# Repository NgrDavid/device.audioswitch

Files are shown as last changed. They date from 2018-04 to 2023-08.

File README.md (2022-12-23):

## Harp AudioSwitch ##

This is a multiplexer device that allows an analog input signal to be forwarded to several output channels. It allows forwarding an audio signal to a single speaker or a combination of speakers. The configuration of speakers can be predefined by software or by using a set of digital inputs.

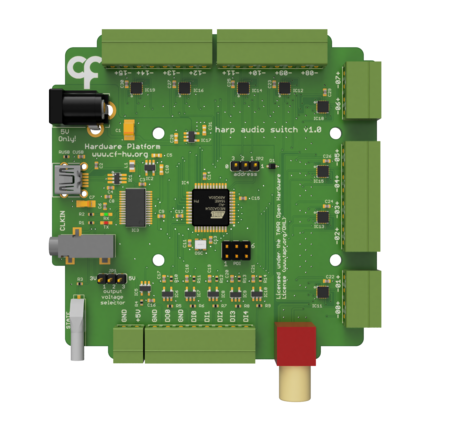
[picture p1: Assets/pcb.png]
harpaudioswitch


### Key Features ###

* Configuration of up to 15 speakers (depending on the input signal strength)
* Several speakers can be activated concurrently

### Connectivity ###

* 1x stereo jack for clock sync input (CLKIN)
* 1x USB (for computer) 1x power barrel connector jack (5V only) 1x screw terminal connector for output power (GND, +5V) 1x screw terminal connector for speaker configuration (GND, DOUT0, GND, DIN0 to DIN4)

## Interface ##

The interface with the Harp board can be done through [Bonsai](https://bonsai-rx.org/) or a dedicated GUI (Graphical User Interface).

In order to use this GUI, there are some software that needs to be installed:

1 - Install the [drivers](https://bitbucket.org/fchampalimaud/downloads/downloads/UsbDriver-2.12.26.zip).

2 - Install the [runtime](https://bitbucket.org/fchampalimaud/downloads/downloads/Runtime-1.0.zip).

3 - Reboot the computer.

4 - Install the [GUI](https://bitbucket.org/fchampalimaud/downloads/downloads/Harp%20Audio%20Switch%20v1.0.0.zip).

## Licensing ##

Each subdirectory will contain a license or, possibly, a set of licenses if it involves both hardware and software.

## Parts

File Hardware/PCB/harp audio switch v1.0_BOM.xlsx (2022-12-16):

Part(s) | Quantity | Description | Distributor | Part. No.
IC1 | 1 | ESD Protection Low Cap | Mouser | 511-USBLC6-2SC6Y
IC2, IC17 | 2 | LDO 250mA Ultra-Lo Noise LDO Reg 3V | Mouser | 595-LP5907MFX-3.0NPB
IC3 | 1 | IC USB USB to Serial UART Enhanced IC SSOP-28 | Mouser | 895-FT232RL
IC4 | 1 | Microcontroladores de 8 bits - MCU 44TQFP, IND TEMP GREEN, 1.6-3.6V | Mouser | 556-ATXMEGA128A4U-AU
IC5, IC6, IC7, IC8, IC9, IC10 | 6 | Buffers e line drivers 1.65-5.5V Single Non-Inverting TTL | Mouser | 863-M74VHC1GT50DTT1G
IC10, IC11, IC12, IC13, IC14, IC15, IC16, IC18 | 8 | CIs de Chave Analógica Quad-SPDT Clickless Audio Switch | Mouser | 700-MAX4910ETE
 | 0 | LDO 250mA Ultra-Lo Noise LDO Reg | Mouser | 595-LP5907MFX-2.8NPB
C3, C4 | 2 | CAP CER 47pF 50V ±5% C0G 0402 | Mouser | 77-VJ0402A470JXACBC
CUSB | 1 | CAP CER 4.7nF 100V ±10% X7R 0402 | Mouser | 81-GRM155R72A472KA01
C22, C23, C24, C25, C26, C27, C29, C30 | 8 | CAP CER 10nF 10V ±10% X5R 0402 | Mouser | 81-GRM155R61A103KA1D
C2, C6, C8, C9, C11, C12, C14, C15, C16, C17, C18, C19, C20, C21 | 14 | CAP CER 100nF 10V X5R 0402 | REEL | REEL
C13 | 1 | CAP CER 0.33uF 10V ±10% X5R 0402 | Mouser | GRM155R61A334KE15D
C7 | 1 | CAP TAN 4.7uF 16V ±10% 1206 | Mouser | 80-T491A475K16AT7280
C5, C10, C28, C31 | 4 | CAP CER 10uF 10V ±10% X5R 0603 | Mouser | 81-GRM188R61A106KE9D
C1 | 1 | CAP TAN 22uF 20V ±10% 1210 | Mouser | 667-20TQC22MYFB
R4, R10, R11, R12, R13, R14 | 6 | RES SMD 33Ω 5% 0402 | Mouser | 667-ERJ-2GEJ330X
R3 | 1 | RES SMD 68Ω 5% 0402 | Mouser | 71-CRCW0402-68-E3
R5, R6, R7, R8, R9 | 5 | RES SMD 100kΩ 1% 0402 | REEL | REEL
RUSB | 1 | RES SMD 1MΩ 1% 0402 | Mouser | 652-CR0402FX-1004GLF
D1 | 1 | DIODE SCHOTTKY 30V 1A SOD323 | Mouser | 621-SDM100K30L-7
STATE | 1 | LED, Green, 1.6mm x 0.8mm, 566 nm, 2.1 V, 20 mA, 15 mcd | Mouser | 78-TLMP1100-GS08
OSC | 1 | 32MHz 10ppm | Mouser | 998-1001CI5032.0000T
CLKIN | 1 | SMT 3.5 STEREO REEL | Mouser | 502-35RASMT2BHNTRX
L1 | 1 | 40ohms 100MHz 1.5A Monolithic 0805 SMD | Mouser | 875-MI0805K400R-10
PDI | 1 | 6P DR UNSHRD HRD | Mouser | 649-67996-206HLF
J1 | 1 | Conectores de fono RCA 1 POS RA PHONO JACK | Mouser | 502-PJRAN1X1U03AUX
USB | 1 | UX60-MB-5S8 | Mouser | 798-UX60-MB-5S8
USB Cable | 1 | USB A - MINI-B 1M BLACK | Mouser | 538-88732-8602
 | 1 | Tubos de Luz LED CML LIGHTPIPE | Mouser | 606-7513D2-L
JACK | 1 | CC 2.5mm LOCKING | Mouser | 161-0725-E
JP1, JP2 | 2 | 3POS Gold Male | Mouser | 649-68001-203HLF
 | 2 | SHUNT JUMPER, 2POS | Farnell | 2396301
WALL ADAPTER | 1 | AC/DC Power Supply, 1 Output, 5 W, 5 V, 1 A | Farnell | 1971787
X1 | 1 | 20.1550M/2-E - Pluggable Terminal Block, 3.5 mm, 2 Ways, 28 AWG, 16 AWG, 1.5 mm², Screw | Farnell | 2575215
X5, X7 | 2 | 20.1550M/4-E - Pluggable Terminal Block, 3.5 mm, 4 Ways, 28 AWG, 16 AWG, 1.5 mm², Screw | Farnell | 2575217
X2, X3, X4, X6 | 4 | 20.1550M/8-E - Pluggable Terminal Block, 3.5 mm, 8 Ways, 28 AWG, 16 AWG, 1.5 mm², Screw | Farnell | 2575220
 | 1 | 20.155MH/2-E - Terminal Block, Horizontal, Header, 3.5 mm, 2 Ways, 10 A | Farnell | 2517858
 | 2 | 20.155MH/4-E - Terminal Block, Horizontal, Header, 3.5 mm, 4 Ways, 10 A | Farnell | 2517860
 | 4 | 20.155MH/8-E - Terminal Block, Horizontal, Header, 3.5 mm, 8 Ways, 10 A | Farnell | 2517863
 | 8 | 1110030 - Nut, Hex, M3, Nylon 6.6, Pack of 50 | Farnell | 1110030
 | 4 | Machine Screw, M3, 10 mm, Nylon (Polyamide), Pan Head Slotted, PK25 | Farnell | 1514410
Components | 106
Licensed under the TAPR Open Hardware License (www.tapr.org/OHL)
Copyright 2017 Artur Silva and Filipe Carvalho

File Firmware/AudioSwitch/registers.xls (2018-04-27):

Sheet: registers
Has event. | When | Type | Array | Array Len. | Register Name | Desciption | Mask Type | Value | Name | Desciption
no |  | U8 | no |  | SOURCE | Source of the board control | mask | (1<<0) | SOURCE
 |  |  |  |  |  |  | group_mask | (0<<0) | USB | Device is controlled by a host computer
 |  |  |  |  |  |  | group_mask | (1<<0) | EXTERNAL | Device is controlled by the digital inputs
yes | When changed by the digital inputs 0-3 | U16 | no |  | CHANNEL_SEL | Enable bit mask of the outputs
yes | When the inputs change (DI0-3 only if they are configured as digital ) | U8 | no |  | DI_STATE | State of the digital inputs | bit | (1<<0) | DI0
 |  |  |  |  |  |  | bit | (1<<1) | DI1
 |  |  |  |  |  |  | bit | (1<<2) | DI2
 |  |  |  |  |  |  | bit | (1<<3) | DI3
 |  |  |  |  |  |  | bit | (1<<4) | DI4
no |  | U8 | no |  | DO | State of the digital output 0 | bit | (1<<0) | DO0
no |  | U8 | no |  | RESERVED0 | Reserved for future use
no |  | U8 | no |  | DI4_CONF | Configuration of digital input 4 (DI4)functionality | mask | (1<<0) | DI4_CONF
 |  |  |  |  |  |  | group_mask | (0<<0) | DI4_DIGITAL
 |  |  |  |  |  |  | group_mask | (1<<0) | DI4_ADDRESS
no |  | U8 | no |  | DO0_CONF | Configuration of the digital output 0 (DO0) funtionality | mask | (1<<0) | DO0_CONF
 |  |  |  |  |  |  | group_mask | (0<<0) | DO_DIGITAL
 |  |  |  |  |  |  | group_mask | (1<<0) | DO_TGL_WHEN_CH_SEL_CHANGE
no |  | U8 | no |  | EVNT_ENABLE | Enable the Events | bit | (1<<0) | EVT_OUTPUT_CHANNEL | Event of register CHANNEL_SEL
 |  |  |  |  |  |  | bit | (1<<1) | EVT_DI_STATE | Event of register DI_STATE

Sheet: meta data
who am I: | 1248
firmware major version: | 1
firmware minor version: | 0
hardware major version: | 1
hardware minor version: | 0
assembly version: | 0
device name: | AudioSwitch

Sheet: ios
Pin Name | PORT | Pin | Direction | Use Input | Out | Out default | Pull | Sense | Int. priority | Int. number | Desciption | Neg. Output
EN0 | PORTA | 0 | output | yes | digital | 0 |  |  |  |  | Enable channel 0 | no
EN1 | PORTA | 1 | output | yes | digital | 0 |  |  |  |  | Enable channel 1 | no
EN2 | PORTA | 2 | output | yes | digital | 0 |  |  |  |  | Enable channel 2 | no
EN3 | PORTA | 3 | output | yes | digital | 0 |  |  |  |  | Enable channel 3 | no
EN4 | PORTA | 4 | output | yes | digital | 0 |  |  |  |  | Enable channel 4 | no
EN5 | PORTA | 5 | output | yes | digital | 0 |  |  |  |  | Enable channel 5 | no
EN6 | PORTA | 6 | output | yes | digital | 0 |  |  |  |  | Enable channel 6 | no
EN7 | PORTA | 7 | output | yes | digital | 0 |  |  |  |  | Enable channel 7 | no
EN8 | PORTD | 0 | output | yes | digital | 0 |  |  |  |  | Enable channel 8 | no
EN9 | PORTD | 1 | output | yes | digital | 0 |  |  |  |  | Enable channel 9 | no
EN10 | PORTD | 2 | output | yes | digital | 0 |  |  |  |  | Enable channel 10 | no
EN11 | PORTD | 3 | output | yes | digital | 0 |  |  |  |  | Enable channel 11 | no
EN12 | PORTD | 4 | output | yes | digital | 0 |  |  |  |  | Enable channel 12 | no
EN13 | PORTD | 5 | output | yes | digital | 0 |  |  |  |  | Enable channel 13 | no
EN14 | PORTD | 6 | output | yes | digital | 0 |  |  |  |  | Enable channel 14 | no
EN15 | PORTD | 7 | output | yes | digital | 0 |  |  |  |  | Enable channel 15 | no
IN0 | PORTB | 0 | input |  |  |  | tristate | both_edges | low | 0 | Decoder bit 0
IN1 | PORTB | 1 | input |  |  |  | tristate | both_edges | low | 0 | Decoder bit 1
IN2 | PORTB | 2 | input |  |  |  | tristate | both_edges | low | 0 | Decoder bit 2
IN3 | PORTB | 3 | input |  |  |  | tristate | both_edges | low | 0 | Decoder bit 3
IN4 | PORTC | 0 | input |  |  |  | tristate | both_edges | low | 0 | Digital Input 4
DO0 | PORTC | 1 | output | yes | digital | 0 |  |  |  |  | Digital output 0 | no
ADD | PORTC | 4 | input |  |  |  | down | both_edges | low | 1 | Address

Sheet: options
Array | Type | Array | Bits type | Direction | Use input | Pull | Sense | Int. priority | Int. number | Int. Mask | Out | Neg. Output
 |  |  |  | input | yes | up | both_edges | low | 0 |  | digital | yes
yes | U8 | yes | bit | output | no | down | rising_edge | med | 1 |  | wire_or | no
no | U16 | no | mask |  |  | tristate | falling_edge | high |  |  | wire_and
 | U32 |  | group_mask |  |  | busholder | low_level | off |  |  | wired_or_pull
 | U64 |  |  |  |  |  | no_interrupt |  |  |  | wired_and_pull
 | I8
 | I16
 | I32
 | I64
 | FLOAT

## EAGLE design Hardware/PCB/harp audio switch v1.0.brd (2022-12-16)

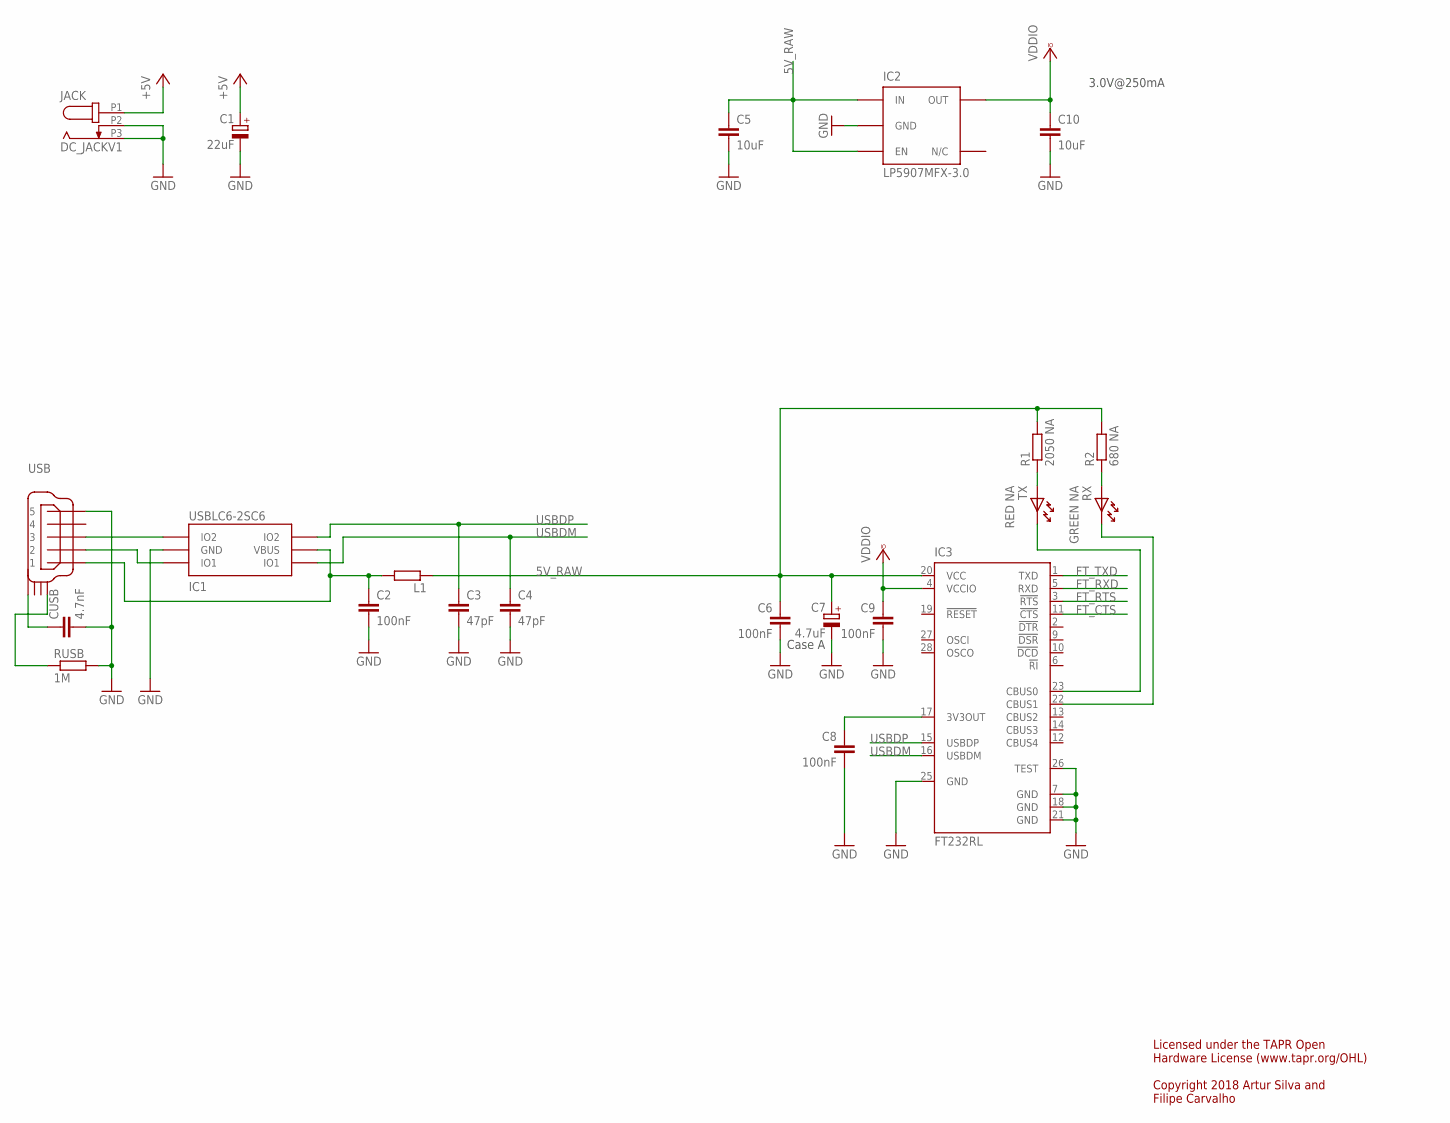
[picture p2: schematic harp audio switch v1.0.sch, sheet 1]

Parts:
C1: 22uF; CAP_100UF_HAND
C2, C6, C8, C9: 100nF; C0402
C3, C4: 47pF; C0402
C5, C10: 10uF; C0603
C7: 4.7uF; A/3216-18W
CUSB: 4.7nF; C0402
IC1: USBLC6-2SC6; SOT23-6L
IC2: LP5907MFX-3.0; TSOT23-5
IC3: FT232RL; SSOP28
JACK: DC_JACKV1; DC_POWER_INPUT
L1: ???; R0805
R1: 2050 NA; R0402
R2: 680 NA; R0402
RUSB: 1M; R0402
RX: GREEN NA; LED_HAND
TX: RED NA; LED_HAND
USB: USB_MINI_B; 240-0002-1

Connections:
5V_RAW: C5.1, C6.1, C7.+, IC2.1 (IN), IC2.3 (EN), IC3.20 (VCC), L1.1, R1.2, R2.2
+5V: C1.+, JACK.P1 (1); also elsewhere on the board
FT_CTS: IC3.11 (!CTS); also elsewhere on the board
FT_RTS: IC3.3 (!RTS); also elsewhere on the board
FT_RXD: IC3.5 (RXD); also elsewhere on the board
FT_TXD: IC3.1 (TXD); also elsewhere on the board
GND: C1.-, C2.2, C3.2, C4.2, C5.2, C6.2, C7.-, C8.2, C9.2, C10.2, CUSB.2, IC1.P$2 (GND), IC2.2 (GND), IC3.7 (GND), IC3.18 (GND), IC3.21 (GND), IC3.25 (GND), IC3.26 (TEST), JACK.P2 (2), JACK.P3 (3), RUSB.2, USB.P$5 (5); also elsewhere on the board
unnamed: C8.1, IC3.17 (3V3OUT)
unnamed: C2.1, IC1.P$5 (VBUS), L1.2, USB.P$1 (1)
unnamed: IC1.P$1 (IO1), USB.P$2 (2)
unnamed: R2.1, RX.A
unnamed: IC3.23 (CBUS0), TX.K
unnamed: IC3.22 (CBUS1), RX.K
unnamed: IC1.P$3 (IO2), USB.P$3 (3)
unnamed: CUSB.1, USB.SHIELD_4
unnamed: RUSB.1, USB.SHIELD_1
unnamed: R1.1, TX.A
USBDM: C4.1, IC1.P$6 (IO1), IC3.16 (USBDM)
USBDP: C3.1, IC1.P$4 (IO2), IC3.15 (USBDP)
VCCIO: C9.1, C10.1, IC2.5 (OUT), IC3.4 (VCCIO); also elsewhere on the board

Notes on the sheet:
Case A
3.0V@250mA
Licensed under the TAPR Open Hardware License (www.tapr.org/OHL) Copyright 2018 Artur Silva and Filipe Carvalho

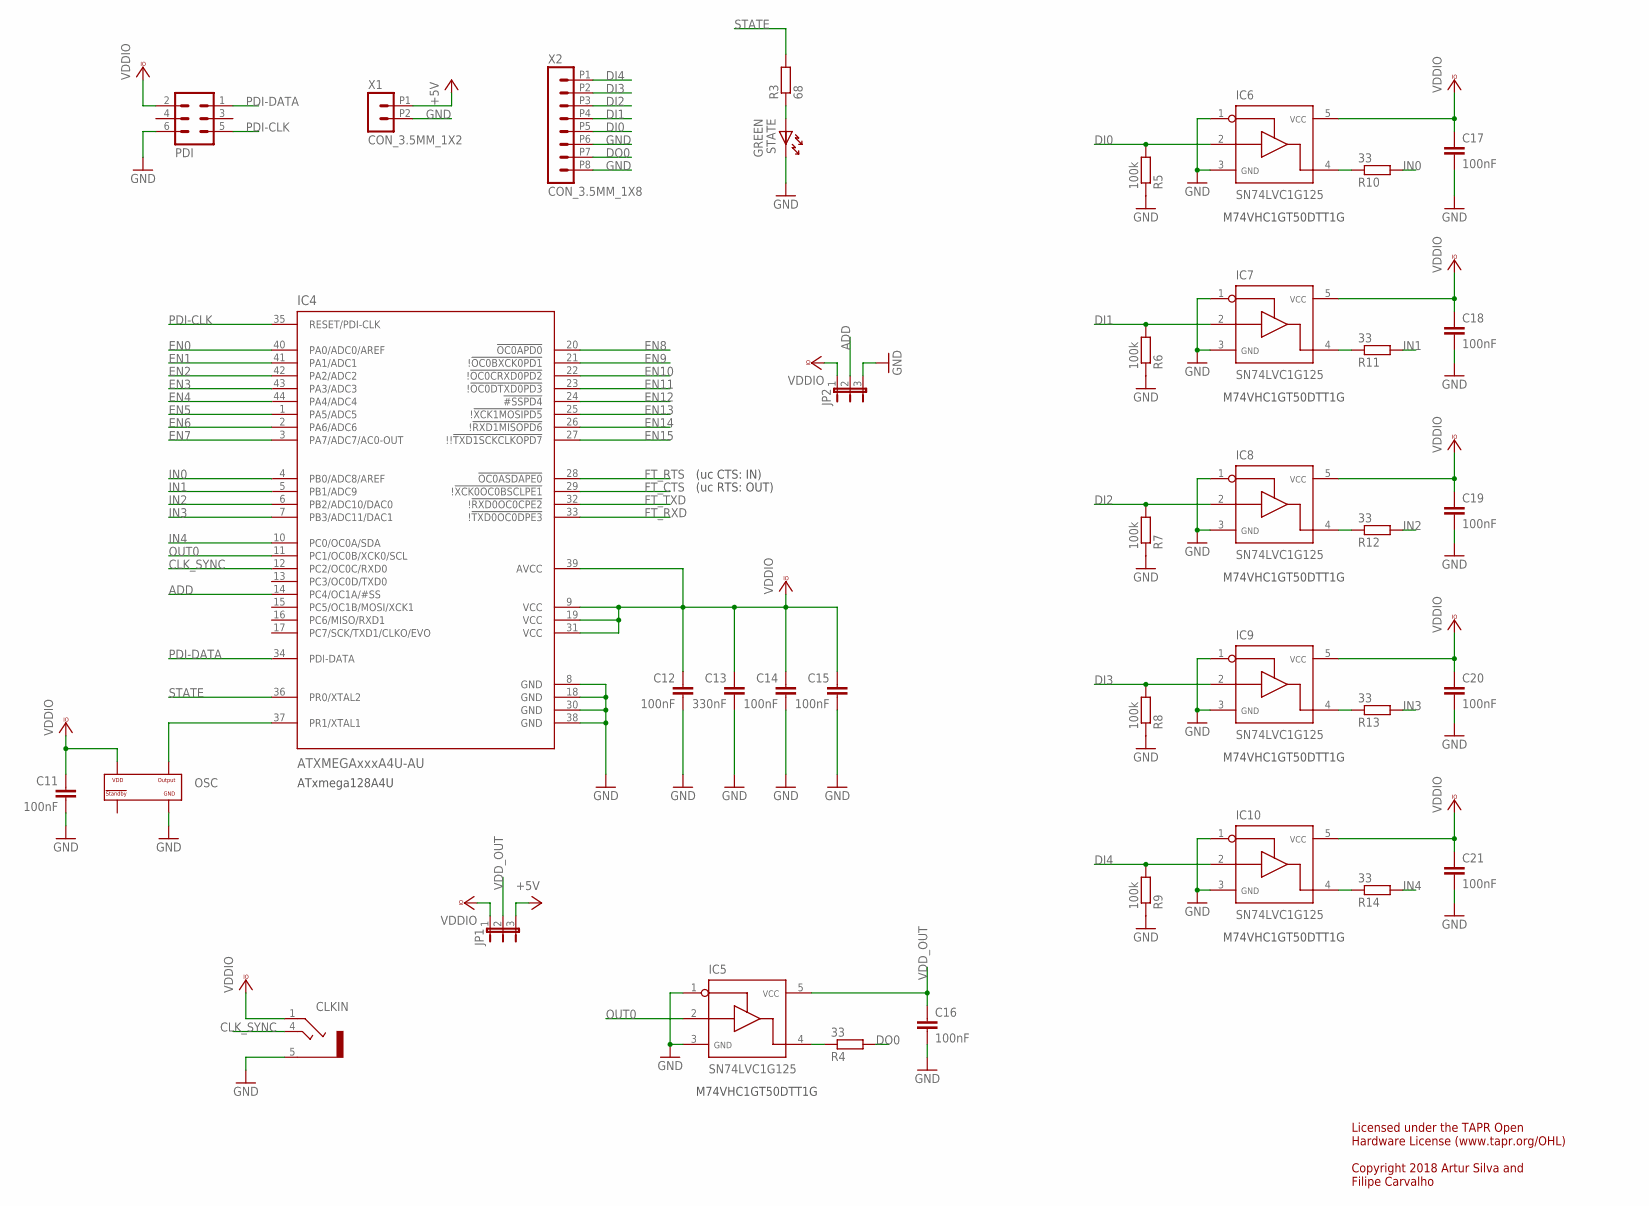
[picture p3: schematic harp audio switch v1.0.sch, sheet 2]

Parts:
C11, C12, C14, C15, C16, C17, C18, C19, C20, C21: 100nF; C0402
C13: 330nF; C0402
CLKIN: STEREO_JACK; 35RASMT2BHNTRX
IC4: ATXMEGAxxxA4U-AU; QFP80P1200X1200X120-44N
IC5, IC6, IC7, IC8, IC9, IC10: SN74LVC1G125; SOT23-5
JP1, JP2: JP2E; JP2
OSC: OSCILLATOR; OSCILLATOR_3.2X2.5
PDI: MA03-2
R3: 68; R0402
R4, R10, R11, R12, R13, R14: 33; R0402
R5, R6, R7, R8, R9: 100k; R0402
STATE: GREEN; LED_HAND
X1: CON_3.5MM_1X2
X2: CON_3.5MM_1X8

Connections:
+5V: JP1.3, X1.P1 (1); also elsewhere on the board
ADD: IC4.14 (PC4/OC1A/#SS), JP2.2
CLK_SYNC: CLKIN.4, IC4.12 (PC2/OC0C/RXD0)
DI0: IC6.2, R5.2, X2.P5 (5)
DI1: IC7.2, R6.2, X2.P4 (4)
DI2: IC8.2, R7.2, X2.P3 (3)
DI3: IC9.2, R8.2, X2.P2 (2)
DI4: IC10.2, R9.2, X2.P1 (1)
DO0: R4.2, X2.P7 (7)
EN0: IC4.40 (PA0/ADC0/AREF); also elsewhere on the board
EN1: IC4.41 (PA1/ADC1); also elsewhere on the board
EN2: IC4.42 (PA2/ADC2); also elsewhere on the board
EN3: IC4.43 (PA3/ADC3); also elsewhere on the board
EN4: IC4.44 (PA4/ADC4); also elsewhere on the board
EN5: IC4.1 (PA5/ADC5); also elsewhere on the board
EN6: IC4.2 (PA6/ADC6); also elsewhere on the board
EN7: IC4.3 (PA7/ADC7/AC0-OUT); also elsewhere on the board
EN8: IC4.20 (!OC0APD0); also elsewhere on the board
EN9: IC4.21 (!!OC0BXCK0PD1); also elsewhere on the board
EN10: IC4.22 (!!OC0CRXD0PD2); also elsewhere on the board
EN11: IC4.23 (!!OC0DTXD0PD3); also elsewhere on the board
EN12: IC4.24 (!#SSPD4); also elsewhere on the board
EN13: IC4.25 (!!XCK1MOSIPD5); also elsewhere on the board
EN14: IC4.26 (!!RXD1MISOPD6); also elsewhere on the board
EN15: IC4.27 (!!!TXD1SCKCLKOPD7); also elsewhere on the board
FT_CTS: IC4.29 (!!XCK0OC0BSCLPE1); also elsewhere on the board
FT_RTS: IC4.28 (!OC0ASDAPE0); also elsewhere on the board
FT_RXD: IC4.33 (!!TXD0OC0DPE3); also elsewhere on the board
FT_TXD: IC4.32 (!!RXD0OC0CPE2); also elsewhere on the board
GND: C11.2, C12.2, C13.2, C14.2, C15.2, C16.2, C17.2, C18.2, C19.2, C20.2, C21.2, CLKIN.5, IC4.8 (GND), IC4.18 (GND), IC4.30 (GND), IC4.38 (GND), IC5.1, IC5.3, IC6.1, IC6.3, IC7.1, IC7.3, IC8.1, IC8.3, IC9.1, IC9.3, IC10.1, IC10.3, JP2.3, OSC.P$2 (GND), PDI.6, R5.1, R6.1, R7.1, R8.1, R9.1, STATE.K, X1.P2 (2), X2.P6 (6), X2.P8 (8); also elsewhere on the board
IN0: IC4.4 (PB0/ADC8/AREF), R10.2
IN1: IC4.5 (PB1/ADC9), R11.2
IN2: IC4.6 (PB2/ADC10/DAC0), R12.2
IN3: IC4.7 (PB3/ADC11/DAC1), R13.2
IN4: IC4.10 (PC0/OC0A/SDA), R14.2
unnamed: IC5.4, R4.1
unnamed: IC7.4, R11.1
unnamed: IC6.4, R10.1
unnamed: IC8.4, R12.1
unnamed: IC9.4, R13.1
unnamed: IC10.4, R14.1
unnamed: R3.1, STATE.A
OSC2: IC4.37 (PR1/XTAL1), OSC.P$3 (OUTPUT)
OUT0: IC4.11 (PC1/OC0B/XCK0/SCL), IC5.2
PDI-CLK: IC4.35 (RESET/PDI-CLK), PDI.5
PDI-DATA: IC4.34 (PDI-DATA), PDI.1
STATE: IC4.36 (PR0/XTAL2), R3.2
VCCIO: C11.1, C12.1, C13.1, C14.1, C15.1, C17.1, C18.1, C19.1, C20.1, C21.1, CLKIN.1, IC4.9 (VCC), IC4.19 (VCC), IC4.31 (VCC), IC4.39 (AVCC), IC6.5, IC7.5, IC8.5, IC9.5, IC10.5, JP1.1, JP2.1, OSC.P$4 (VDD), PDI.2; also elsewhere on the board
VDD_OUT: C16.1, IC5.5, JP1.2

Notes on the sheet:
Licensed under the TAPR Open Hardware License (www.tapr.org/OHL) Copyright 2018 Artur Silva and Filipe Carvalho
(uc CTS: IN)
(uc RTS: OUT)
M74VHC1GT50DTT1G
ATxmega128A4U

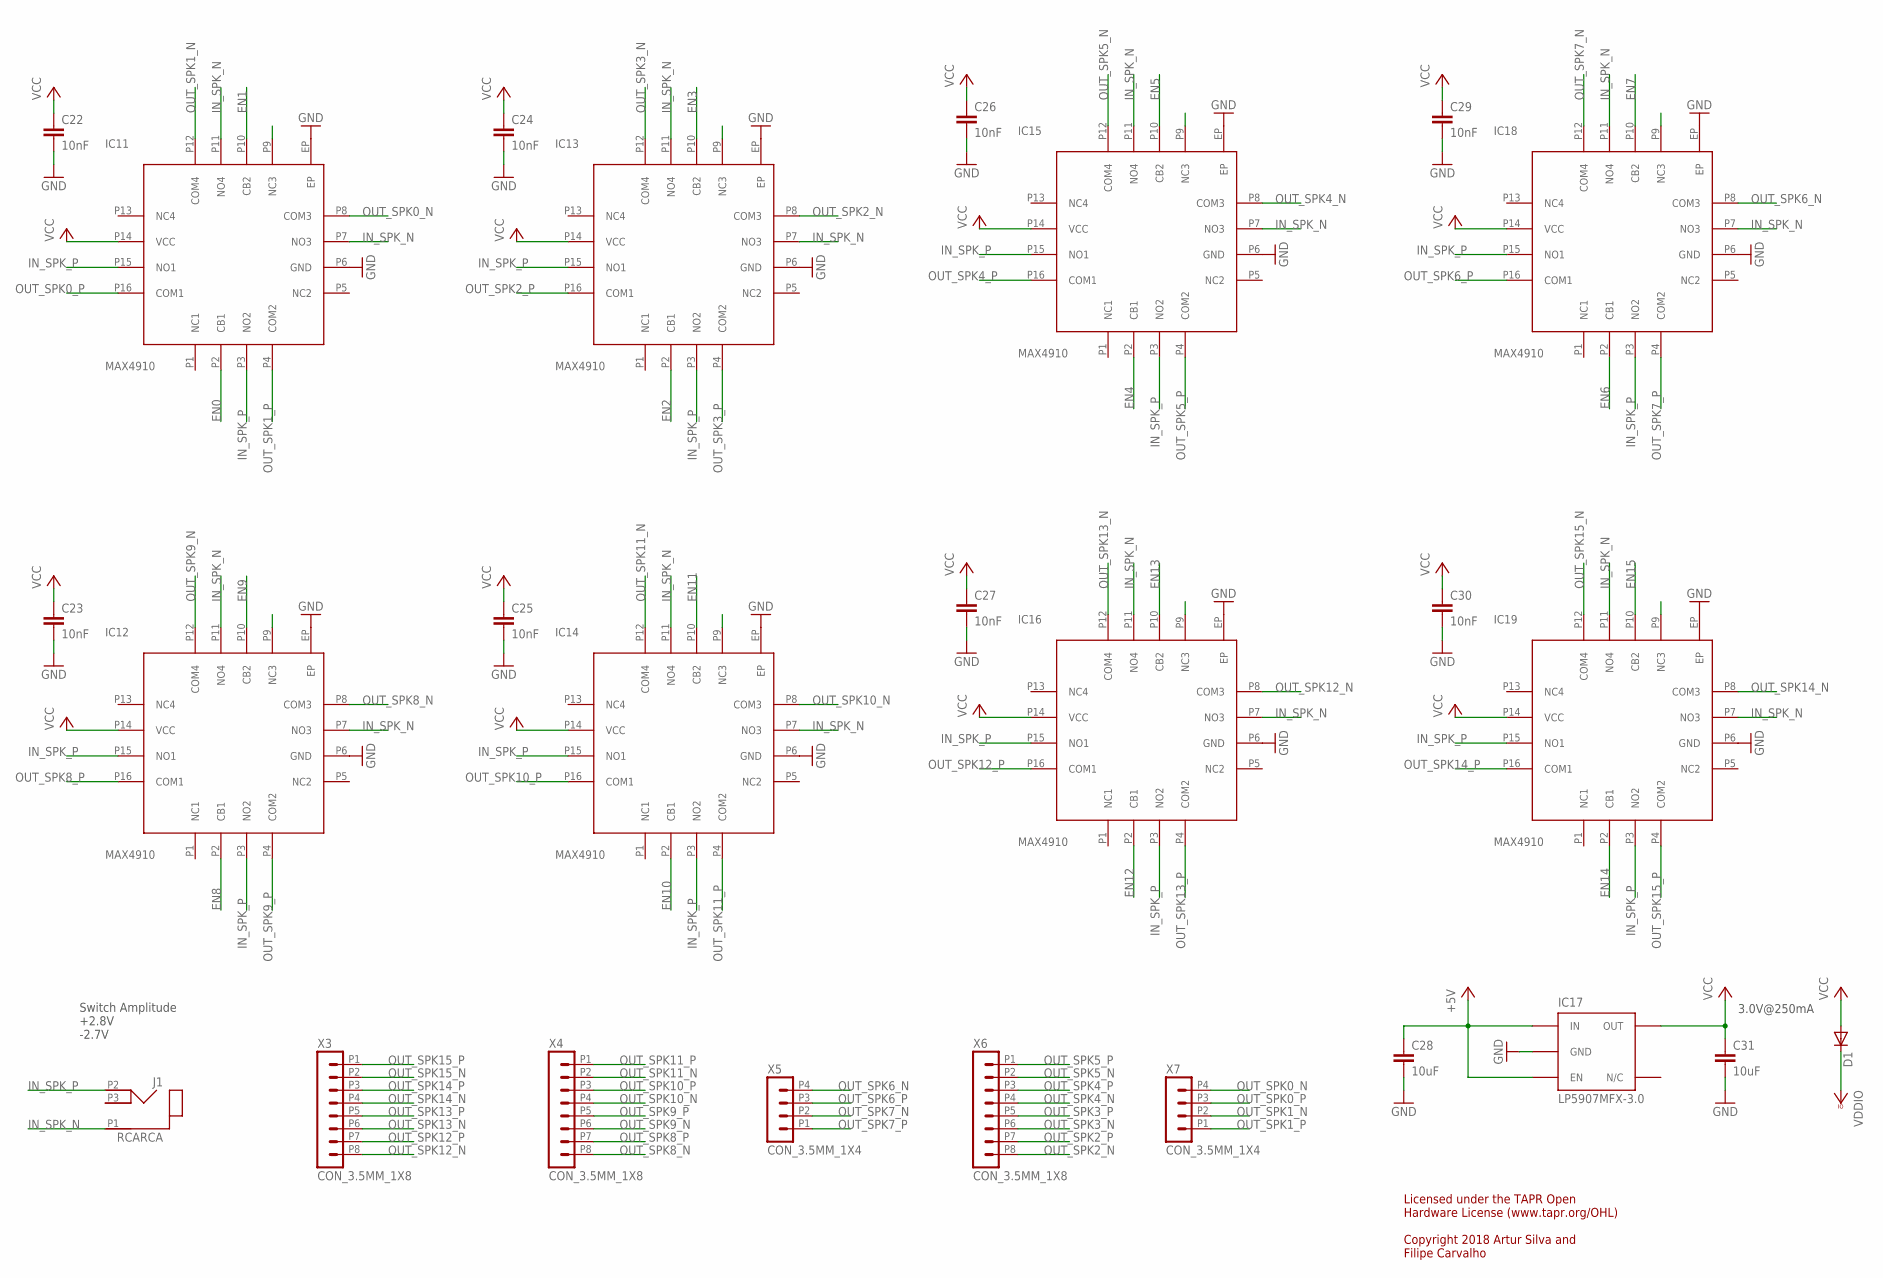
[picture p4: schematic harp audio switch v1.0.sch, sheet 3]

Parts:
C22, C23, C24, C25, C26, C27, C29, C30: 10nF; C0402
C28, C31: 10uF; C0603
D1: DIODE-SOD323-R; SOD323-R
IC11, IC12, IC13, IC14, IC15, IC16, IC18, IC19: MAX4910; QFN16
IC17: LP5907MFX-3.0; TSOT23-5
J1: RCARCA; RCA
X3, X4, X6: CON_3.5MM_1X8
X5, X7: CON_3.5MM_1X4

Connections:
+5V: C28.1, IC17.1 (IN), IC17.3 (EN); also elsewhere on the board
EN0: IC11.P2 (CB1); also elsewhere on the board
EN1: IC11.P10 (CB2); also elsewhere on the board
EN2: IC13.P2 (CB1); also elsewhere on the board
EN3: IC13.P10 (CB2); also elsewhere on the board
EN4: IC15.P2 (CB1); also elsewhere on the board
EN5: IC15.P10 (CB2); also elsewhere on the board
EN6: IC18.P2 (CB1); also elsewhere on the board
EN7: IC18.P10 (CB2); also elsewhere on the board
EN8: IC12.P2 (CB1); also elsewhere on the board
EN9: IC12.P10 (CB2); also elsewhere on the board
EN10: IC14.P2 (CB1); also elsewhere on the board
EN11: IC14.P10 (CB2); also elsewhere on the board
EN12: IC16.P2 (CB1); also elsewhere on the board
EN13: IC16.P10 (CB2); also elsewhere on the board
EN14: IC19.P2 (CB1); also elsewhere on the board
EN15: IC19.P10 (CB2); also elsewhere on the board
GND: C22.2, C23.2, C24.2, C25.2, C26.2, C27.2, C28.2, C29.2, C30.2, C31.2, IC11.EP, IC11.P6 (GND), IC12.EP, IC12.P6 (GND), IC13.EP, IC13.P6 (GND), IC14.EP, IC14.P6 (GND), IC15.EP, IC15.P6 (GND), IC16.EP, IC16.P6 (GND), IC17.2 (GND), IC18.EP, IC18.P6 (GND), IC19.EP, IC19.P6 (GND); also elsewhere on the board
IN_SPK_N: IC11.P7 (NO3), IC11.P11 (NO4), IC12.P7 (NO3), IC12.P11 (NO4), IC13.P7 (NO3), IC13.P11 (NO4), IC14.P7 (NO3), IC14.P11 (NO4), IC15.P7 (NO3), IC15.P11 (NO4), IC16.P7 (NO3), IC16.P11 (NO4), IC18.P7 (NO3), IC18.P11 (NO4), IC19.P7 (NO3), IC19.P11 (NO4), J1.P1 (1)
IN_SPK_P: IC11.P3 (NO2), IC11.P15 (NO1), IC12.P3 (NO2), IC12.P15 (NO1), IC13.P3 (NO2), IC13.P15 (NO1), IC14.P3 (NO2), IC14.P15 (NO1), IC15.P3 (NO2), IC15.P15 (NO1), IC16.P3 (NO2), IC16.P15 (NO1), IC18.P3 (NO2), IC18.P15 (NO1), IC19.P3 (NO2), IC19.P15 (NO1), J1.P2 (2)
OUT_SPK0_N: IC11.P8 (COM3), X7.P4 (4)
OUT_SPK0_P: IC11.P16 (COM1), X7.P3 (3)
OUT_SPK1_N: IC11.P12 (COM4), X7.P2 (2)
OUT_SPK1_P: IC11.P4 (COM2), X7.P1 (1)
OUT_SPK2_N: IC13.P8 (COM3), X6.P8 (8)
OUT_SPK2_P: IC13.P16 (COM1), X6.P7 (7)
OUT_SPK3_N: IC13.P12 (COM4), X6.P6 (6)
OUT_SPK3_P: IC13.P4 (COM2), X6.P5 (5)
OUT_SPK4_N: IC15.P8 (COM3), X6.P4 (4)
OUT_SPK4_P: IC15.P16 (COM1), X6.P3 (3)
OUT_SPK5_N: IC15.P12 (COM4), X6.P2 (2)
OUT_SPK5_P: IC15.P4 (COM2), X6.P1 (1)
OUT_SPK6_N: IC18.P8 (COM3), X5.P4 (4)
OUT_SPK6_P: IC18.P16 (COM1), X5.P3 (3)
OUT_SPK7_N: IC18.P12 (COM4), X5.P2 (2)
OUT_SPK7_P: IC18.P4 (COM2), X5.P1 (1)
OUT_SPK8_N: IC12.P8 (COM3), X4.P8 (8)
OUT_SPK8_P: IC12.P16 (COM1), X4.P7 (7)
OUT_SPK9_N: IC12.P12 (COM4), X4.P6 (6)
OUT_SPK9_P: IC12.P4 (COM2), X4.P5 (5)
OUT_SPK10_N: IC14.P8 (COM3), X4.P4 (4)
OUT_SPK10_P: IC14.P16 (COM1), X4.P3 (3)
OUT_SPK11_N: IC14.P12 (COM4), X4.P2 (2)
OUT_SPK11_P: IC14.P4 (COM2), X4.P1 (1)
OUT_SPK12_N: IC16.P8 (COM3), X3.P8 (8)
OUT_SPK12_P: IC16.P16 (COM1), X3.P7 (7)
OUT_SPK13_N: IC16.P12 (COM4), X3.P6 (6)
OUT_SPK13_P: IC16.P4 (COM2), X3.P5 (5)
OUT_SPK14_N: IC19.P8 (COM3), X3.P4 (4)
OUT_SPK14_P: IC19.P16 (COM1), X3.P3 (3)
OUT_SPK15_N: IC19.P12 (COM4), X3.P2 (2)
OUT_SPK15_P: IC19.P4 (COM2), X3.P1 (1)
VCC: C22.1, C23.1, C24.1, C25.1, C26.1, C27.1, C29.1, C30.1, C31.1, D1.A, IC11.P14 (VCC), IC12.P14 (VCC), IC13.P14 (VCC), IC14.P14 (VCC), IC15.P14 (VCC), IC16.P14 (VCC), IC17.5 (OUT), IC18.P14 (VCC), IC19.P14 (VCC)
VCCIO: D1.C; also elsewhere on the board

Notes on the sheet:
Licensed under the TAPR Open Hardware License (www.tapr.org/OHL) Copyright 2018 Artur Silva and Filipe Carvalho
3.0V@250mA
Switch Amplitude +2.8V -2.7V

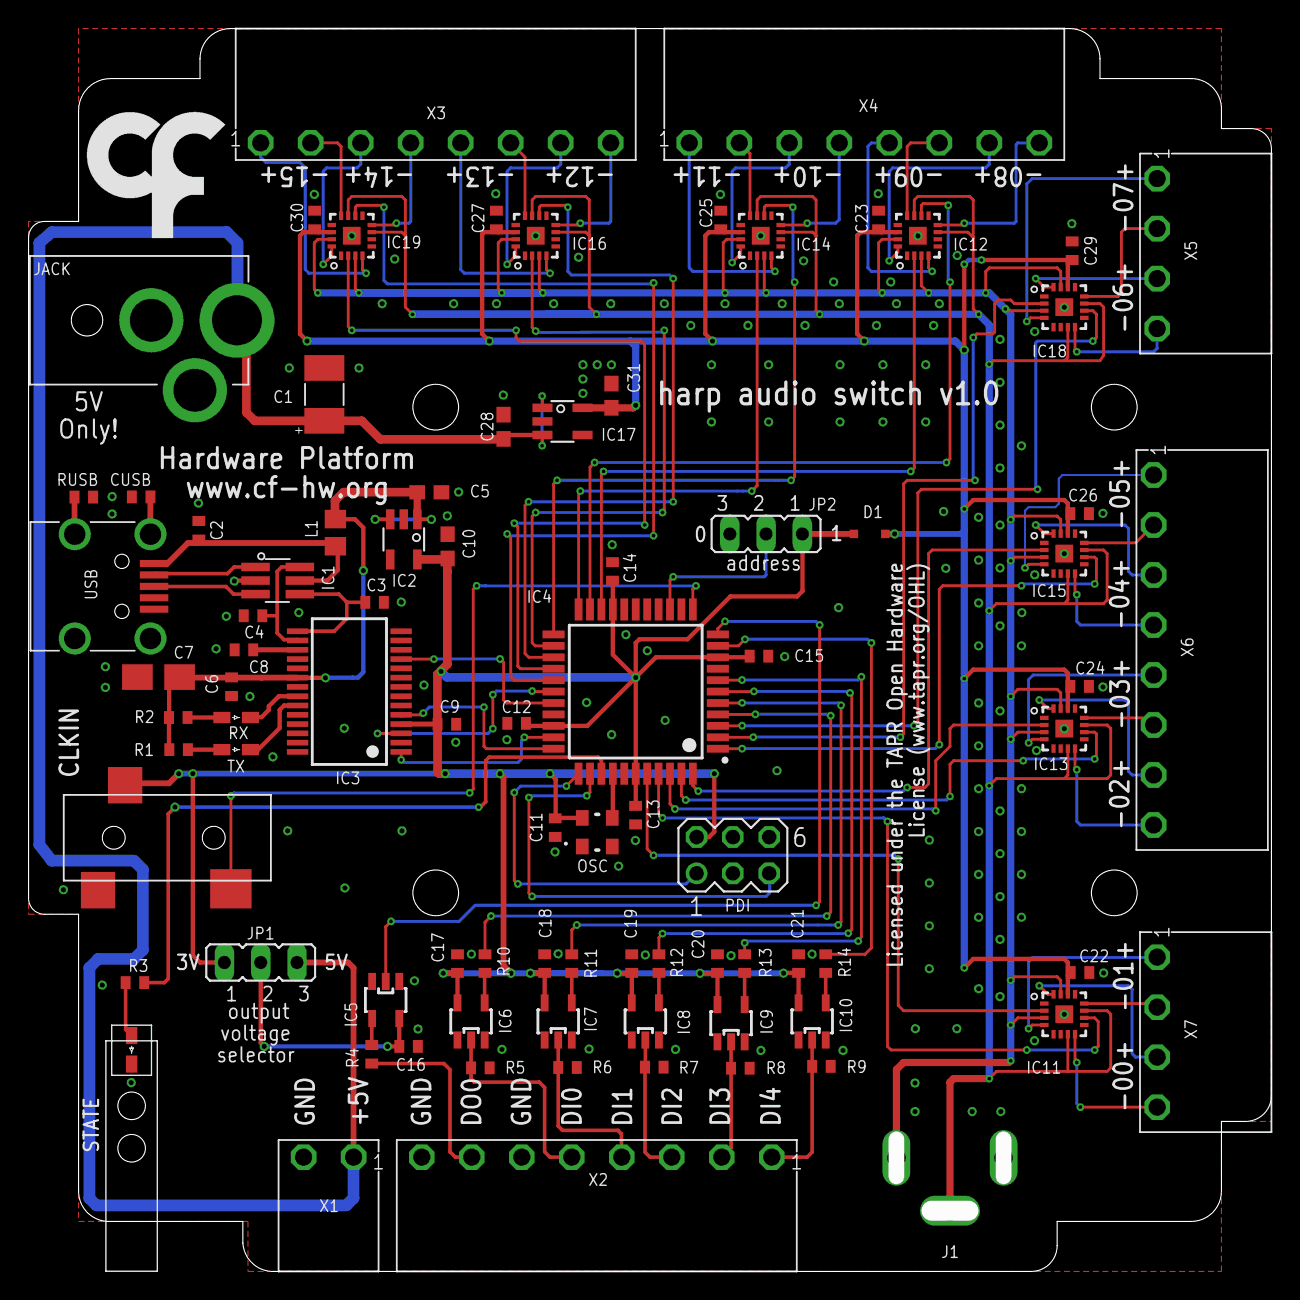
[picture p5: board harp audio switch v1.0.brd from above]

Board: 2 copper layers, 87.0 x 87.0 mm, 89 parts (1 on the bottom side), 97 nets.

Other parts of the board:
U$1: LED_PIPE_7513D2-L
U$3: LOGO_5
U$9: LOGO_6

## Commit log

2018-04-24 Initial commit.
    [registers.xls]
2018-04-24 Corrected device ID to 1248.
    [registers.xls]
2018-04-27 Removed bit B_EVT_DO from the bits list.
    [registers.xls]
2018-04-27 Added filter to the digital inputs.
2022-12-16 Add PCB and BOM files
    [harp audio switch v1.0.brd, harp audio switch v1.0.sch, harp audio switch v1.0_BOM.xlsx]
2022-12-23 refactor repository structure
    [harp audio switch v1.0.brd, harp audio switch v1.0.sch, harp audio switch v1.0_BOM.xlsx]
2023-05-10 Add PCB image
2023-08-09 update device.yml with channels bitmask
2023-08-19 Reduce PCB image dimensions
2023-09-14 Update device.yml firmware version
2024-11-13 Update device schema source
2024-11-21 add missing asset for device interface
